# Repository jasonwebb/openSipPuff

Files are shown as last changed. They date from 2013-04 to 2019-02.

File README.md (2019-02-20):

# openSip+Puff

__openSip+Puff__ aims to provide a cheap, simple, open, and modern alternative input method based on the breath of a user that can be easily mapped to a variety of common actions like mouse clicks and keypresses.

The ultimate goal of this project is to go beyond simple utilitarian functionality and provide a new modality for creative expression that is meaningful for people with or without limited mobility. For me this means musical expression and visual art applications, but you are welcome to take it in whatever direction you want!

In contrast to other DIY sip-and-puff solutions, this project aims to keep the number of parts and assembly steps to a minimum while keeping the focus entirely on the digitization of breath - nothing more, nothing less. The hope is that this device can be manufactured as a true "plug-and-play", standalone device such that the only remaining steps that users will need to complete on their own are to (1) pop the board into an enclosure, (2) attach a mouthpiece with tubing, and (3) plug in a USB cable. With the help of native USB HID functionality, this device should (theoretically) be as easy to set up as any keyboard or mouse - no special drivers needed!

In keeping the focus tight and the parts count low it is expected that this device will be possible to sell for under $100 (ideally around $60). Fewer external parts also means fewer points of failure, so the device should last a while with minimal need for maintenance.

## Features
### Hardware
* ATmega32u4 microcontroller running the [Arduino Leonardo bootloader](https://www.arduino.cc/en/Main/ArduinoBoardLeonardo), allowing for the device to work as a standard USB HID device (mouse, keyboard, MIDI, etc) without any special drivers.
* [MPXV7007GP](https://www.digikey.com/product-detail/en/nxp-usa-inc/MPXV7007GP/MPXV7007GP-ND/1168441) analog pressure sensor for detecting direction and strength of sips and puffs.
* USB mini-B port so it can be connected to any PC
* 4-pin I2C interface for future expansion (may be removed if a good use case isn't identified)

### Firmware
```
TODO:
=====
  1. Sips and puffs need to be associated with actions (keypresses, mouse clicks, MIDI notes, etc) using some 
     sort of persistent data structure that can be loaded from EEPROM when the device is powered on.
  2. Patterns of sips and puffs should also be supported at some point. For example, one puff for left mouse 
     click, two puffs for right mouse click.
  3. Output raw analog values as serial data over USB to be transformed into other interesting actions by custom 
     applications or something like Wekinator.
  4. Output analog data as MIDI CC changes so the device can be used for expressive musical applications.
```

### Software
```
TODO:
=====
To make it easy for non-technical users to reconfigure the device, some sort of easy-to-use desktop application 
should be built. 

Once the firmware is worked out, I'd like to experiment with using Electron and modern web technologies to build 
this interface. 
```

### Mechanical
```
TODO:
=====
Connecting a plain plastic tube directly the sensor is fine for prototyping, but is not hygienic for real-world 
users. Some sort of easy-to-replace filter(s) should be added to capture saliva and particulates before they 
reach the sensor. 

I don't know much about these sorts of filters, so if you have some experience or ideas please send them to me!
```

## Similar projects
When I started building this project there weren't any other viable DIY sip-and-puff interfaces out there, but in the past year so a few great projects have sprung up that are worth looking at!

* [LipSync](https://github.com/makersmakingchange/LipSync) - uses an Arduino Pro Micro board and the [MPXV7002DPT1](https://www.digikey.com/product-detail/en/nxp-usa-inc/MPXV7002DPT1/MPXV7002DPT1CT-ND/3524215) sensor, as well as an optional Bluetooth breakout board. Includes a custom mouth-operated joystick built using 3D-printed parts and FSRs, all housed in a 3D-printed enclosure. _Incredible_ documentation, and available as a kit or fully assembled through [Makers Making Change](https://www.makersmakingchange.com/project/lipsync/).
* [FLipMouse](https://github.com/asterics/FLipMouse) - uses a Teensy LC and the [MPXV7007GP](https://www.digikey.com/product-detail/en/nxp-usa-inc/MPXV7007GP/MPXV7007GP-ND/1168441) sensor. Includes a custom mouth-operated joystick that is nearly identical to LipSync, all housed in a laser-cut acrylic enclosure. Available as a kit through [Hackerspace Shop](https://hackerspaceshop.com/products/flipmouse-diy-kit).
* [The 'Sup](https://www.instructables.com/id/The-Sup-a-Mouse-for-Quadriplegics-Low-Cost-and-Ope/) - uses an Arduino Pro Micro and a [MPXV7002DP](https://www.ebay.com/itm/MD-PS002-MPXV7002DP-Transducer-Pressure-Sensor-Differential-Breakout-Board-/401602810835?oid=202106155765) sensor on a breakout board, as well as an off-the-shelf [two-axis joystick module](https://www.ebay.com/itm/Module-PS2-Lever-Hots-Two-axis-Sensor-Joystick-Game-Controller/302615277464?hash=item467546af98:g:eGQAAOSwKXdaadFS). Features a unique 3D-printed mouthpiece that couples the joystick and tubing, though no filters are used.

## License
This work is licensed under a [Creative Commons Attribution-NonCommercial-ShareAlike 4.0 International License](http://creativecommons.org/licenses/by-nc-sa/4.0/).

Use this project to learn, tinker and share with friends. You are completely free to build this project for individuals  who need it. Small commercial runs for workshops or other educational uses are also completely cool.

The only reason that a fully-permissive open-source license is not used is to discourage, however naively, abuse through mass production and sale of this project by companies who are not as passionate about the quality and core mission of the project. If you're interested in producing and distributing this project to larger markets, please contact me and maybe we can collaborate!



## Media

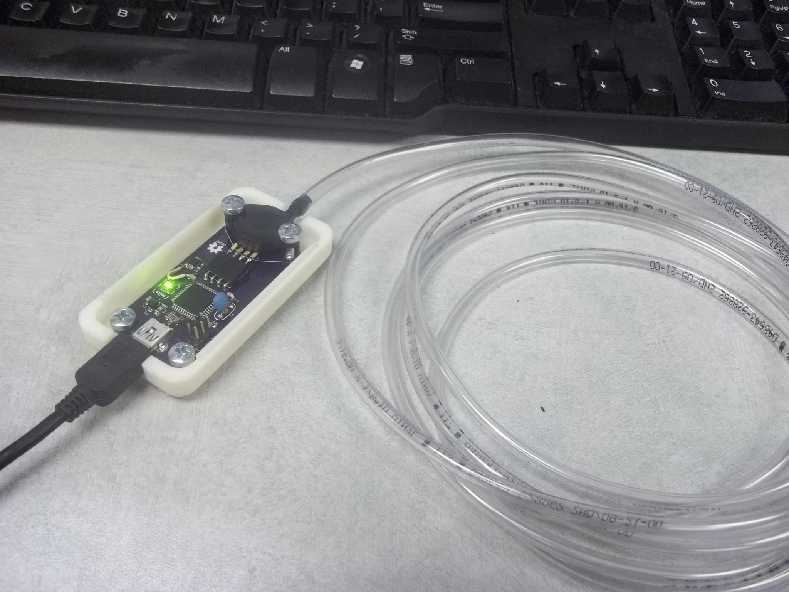
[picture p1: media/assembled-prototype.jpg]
Assembled prototype


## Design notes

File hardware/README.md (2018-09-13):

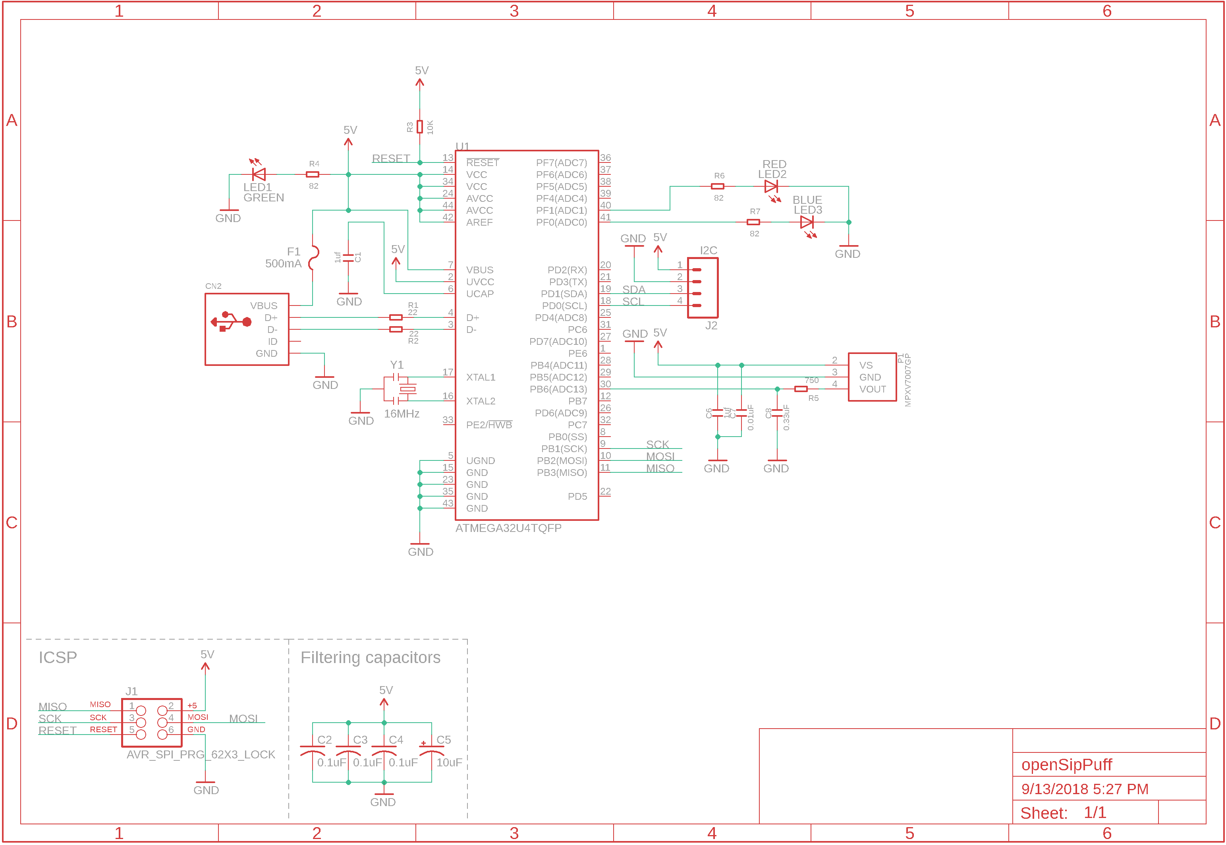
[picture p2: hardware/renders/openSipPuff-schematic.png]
Schematic


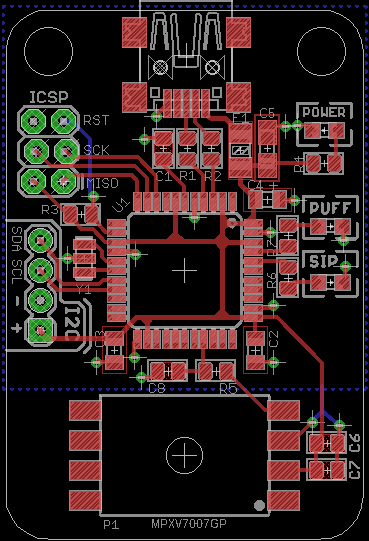
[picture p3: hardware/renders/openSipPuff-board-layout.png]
Board layout


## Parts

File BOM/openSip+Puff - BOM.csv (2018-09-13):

ID | Specifications | Purpose | Cost @ 1 | Cost @ 25 | Cost @ 50 | Cost @ 100 | Part number | URL
C1 | 1uF capacitor (0805) | USB smoothing cap for U1 | $0.28 | $0.19 | $0.19 | $0.11 | 399-8003-1-ND | https://www.digikey.com/product-detail/en/kemet/C0805C105K3PACTU/399-8003-1-ND/3471726
C2 | 0.1uF capacitor (0805) | Power smoothing for U1 | $0.30 | $0.21 | $0.21 | $0.10 | 709-1185-1-ND | https://www.digikey.com/product-detail/en/johanson-dielectrics-inc/250R15W104KV4T/709-1185-1-ND/1859517
C3 | 0.1uF capacitor (0805) | Power smoothing for U1 | $0.30 | $0.21 | $0.21 | $0.10 | 709-1185-1-ND | https://www.digikey.com/product-detail/en/johanson-dielectrics-inc/250R15W104KV4T/709-1185-1-ND/1859517
C4 | 0.1uF capacitor (0805) | Power smoothing for U1 | $0.30 | $0.21 | $0.21 | $0.10 | 709-1185-1-ND | https://www.digikey.com/product-detail/en/johanson-dielectrics-inc/250R15W104KV4T/709-1185-1-ND/1859517
C5 | 10uF polarized tantalum capacitor (1206) | Input power smoothing | $0.41 | $0.28 | $0.28 | $0.17 | 399-3683-1-ND | https://www.digikey.com/product-detail/en/kemet/T491A106K006AT/399-3683-1-ND/819008
C6 | 1uF capacitor (0805) | Power smoothing for P1 | $0.28 | $0.19 | $0.19 | $0.11 | 399-8003-1-ND | https://www.digikey.com/product-detail/en/kemet/C0805C105K3PACTU/399-8003-1-ND/3471726
C7 | 0.01uF capactor (0805) | Power smoothing for P1 | $0.48 | $0.33 | $0.33 | $0.20 | 399-7990-1-ND | https://www.digikey.com/product-detail/en/kemet/C0805C103J3GACTU/399-7990-1-ND/3471713
C8 | 0.33uF capacitor (0805) | Low-pass filter for P1 | $0.20 | $0.15 | $0.15 | $0.07 | 1276-1797-1-ND | https://www.digikey.com/product-detail/en/samsung-electro-mechanics/CL21B334KOCNNNC/1276-1797-1-ND/3889883
CN1 | USB mini-B | USB connector | $0.54 | $0.50 | $0.41 | $0.39 | 151-1206-1-ND | https://www.digikey.com/product-detail/en/edac-inc/690-005-299-043/151-1206-1-ND/4312192
F1 | 500mA PTC fuse | Protect board from spikes over USB, and USB from shorts | $0.13 | $0.13 | $0.11 | $0.10 | 507-1799-1-ND | https://www.digikey.com/product-detail/en/bel-fuse-inc/0ZCJ0025AF2E/507-1799-1-ND/4156322
J1 | 2x3 header (left blank) | ICSP interface
J2 | 1x4 header (left blank) | I2C breakout interface
LED1 | 20mA @ 2V green LED (0805) | Power indicator LED (green) | $0.31 | $0.17 | $0.17 | $0.12 | 160-1426-1-ND | https://www.digikey.com/product-detail/en/lite-on-inc/LTST-C171KGKT/160-1426-1-ND/386798
LED2 | 20mA @ 2V red LED (0805) | Sip indicator LED (red) | $0.35 | $0.19 | $0.19 | $0.13 | 160-1415-1-ND | https://www.digikey.com/product-detail/en/lite-on-inc/LTST-C170KRKT/160-1415-1-ND/386778
LED3 | 20mA @ 3.3V blue LED (0805) | Puff indicator LED (blue) | $0.50 | $0.28 | $0.28 | $0.18 | 160-1645-1-ND | https://www.digikey.com/product-detail/en/lite-on-inc/LTST-C171TBKT/160-1645-1-ND/573585
P1 | MPXV7007GP | Pressure sensor | $17.70 | $13.42 | $13.05 | $13.05 | MPXV7007GP-ND | https://www.digikey.com/products/en?keywords=mpxv7007gp
R1 | 22ohm resistor (0805) | USB termination resistors | $0.10 | $0.05 | $0.05 | $0.02 | 311-22.0CRCT-ND | https://www.digikey.com/product-detail/en/yageo/RC0805FR-0722RL/311-22.0CRCT-ND/730682
R2 | 22ohm resistor (0805) | USB termination resistors | $0.10 | $0.05 | $0.05 | $0.02 | 311-22.0CRCT-ND | https://www.digikey.com/product-detail/en/yageo/RC0805FR-0722RL/311-22.0CRCT-ND/730682
R3 | 10k resistor (0805) | RESET line pullup | $0.17 | $0.14 | $0.14 | $0.05 | RNCF0805DTE10K0CT-ND | https://www.digikey.com/product-detail/en/stackpole-electronics-inc/RNCF0805DTE10K0/RNCF0805DTE10K0CT-ND/2687083
R4 | 150ohm resistor (0805) | Current limit for LED1 | $0.10 | $0.09 | $0.09 | $0.03 | RHM150KCT-ND | https://www.digikey.com/product-detail/en/rohm-semiconductor/ESR10EZPJ151/RHM150KCT-ND/1762967
R5 | 750ohm resistor (0805) |  | $0.36 | $0.30 | $0.30 | $0.12 | P750DACT-ND | https://www.digikey.com/product-detail/en/panasonic-electronic-components/ERA-6AEB751V/P750DACT-ND/1465944
R6 | 150ohm resistor (0805) | Current limit for LED2 | $0.10 | $0.09 | $0.09 | $0.03 | RHM150KCT-ND | https://www.digikey.com/product-detail/en/rohm-semiconductor/ESR10EZPJ151/RHM150KCT-ND/1762967
R7 | 84.5ohm resistor (0805) | Current limit for LED3 | $0.10 | $0.06 | $0.06 | $0.02 | 311-84.5CRCT-ND | https://www.digikey.com/product-detail/en/yageo/RC0805FR-0784R5L/311-84.5CRCT-ND/731119
U1 | ATMega32u4 | Microcontroller | $4.20 | $3.85 | $3.85 | $3.49 | ATMEGA32U4-AURCT-ND | https://www.digikey.com/product-detail/en/microchip-technology/ATMEGA32U4-AUR/ATMEGA32U4-AURCT-ND/3440960
Y1 | 16MHz resonator | Resonator for microcontoller | $0.30 | $0.25 | $0.22 | $0.20 | 490-17948-1-ND | https://www.digikey.com/product-detail/en/murata-electronics-north-america/CSTNE16M0V530000R0/490-17948-1-ND/8747756
 |  | Total | $27.61 | $21.28 | $20.79

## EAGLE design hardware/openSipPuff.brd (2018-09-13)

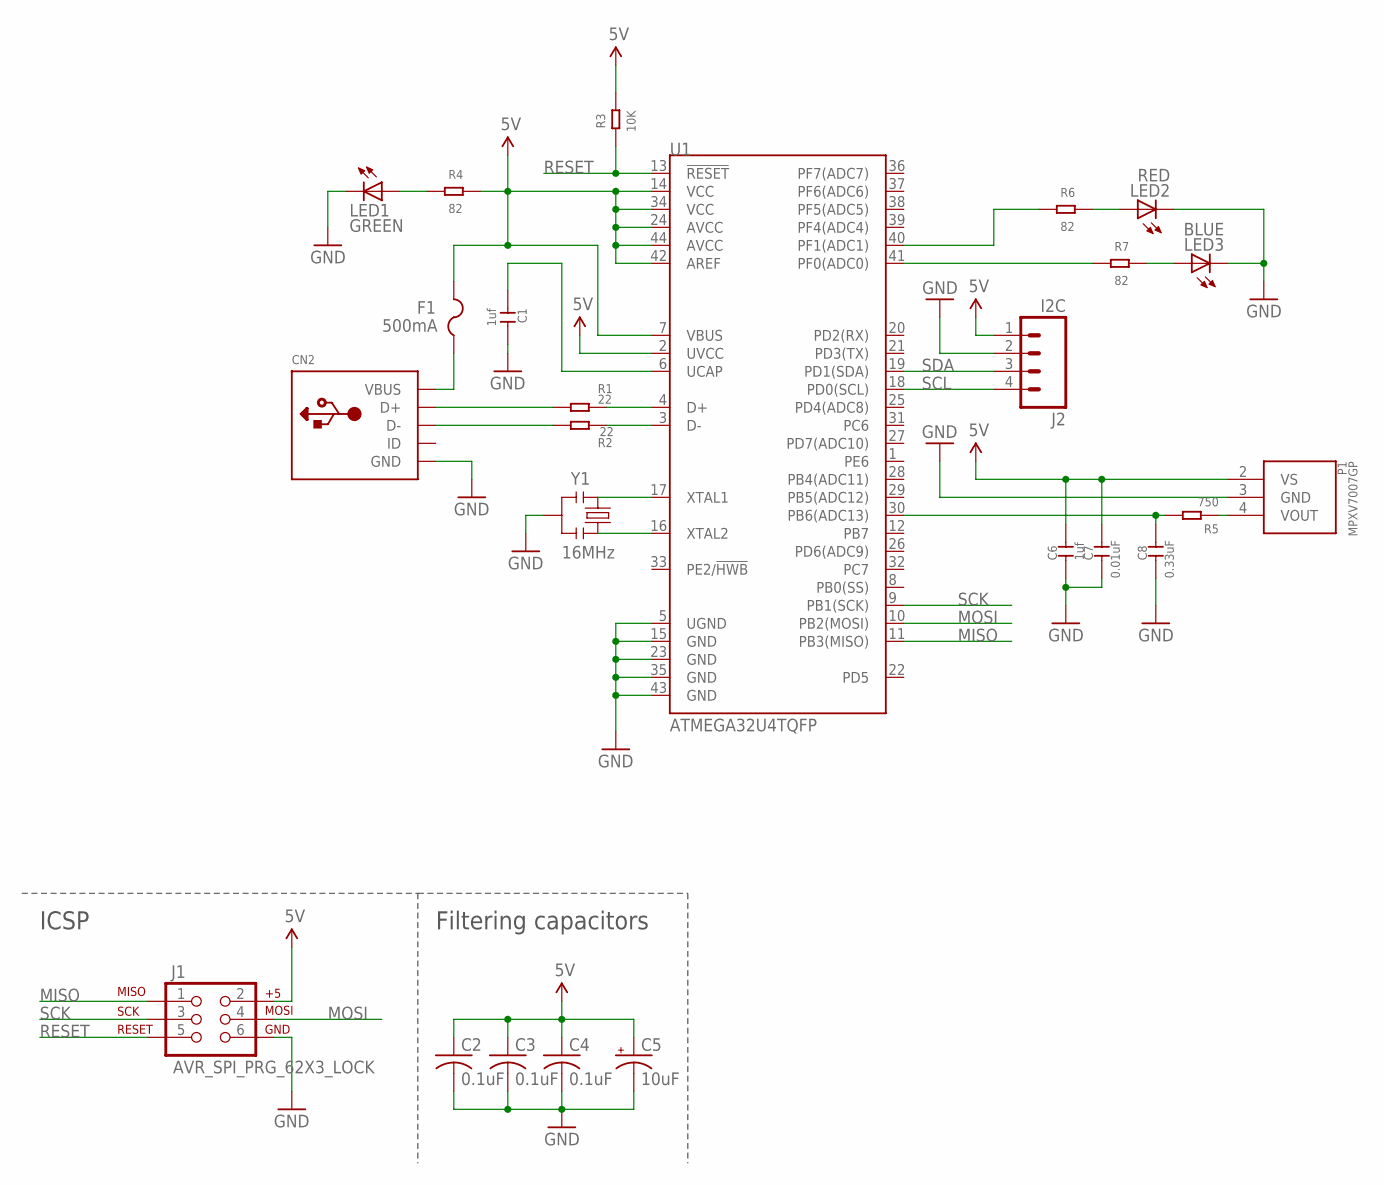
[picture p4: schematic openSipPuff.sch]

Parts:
C1, C6: 1uf; C0805
C2, C3, C4: 0.1uF; C0805K
C5: 10uF; A/3216-18R
C7: 0.01uF; C0805
C8: 0.33uF; C0805
CN2: USBMINIB; USB-MINIB
F1: 500mA; R1206
J1: AVR_SPI_PRG_62X3_LOCK; 2X3_LOCK
J2: I2C; 1X04
LED1: GREEN; CHIPLED_0805
LED2: RED; CHIPLED_0805
LED3: BLUE; CHIPLED_0805
P1: MPXV7007GP; SOP8
R1, R2: 22; R0805
R3: 10K; R0805
R4, R6, R7: 82; R0805
R5: 750; R0805
U1: ATMEGA32U4TQFP; SPARKFUN-DIGITALIC_TQFP44
Y1: 16MHz; RESONATOR-SMD

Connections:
5V: C2.1, C3.1, C4.1, C5.+, C6.2, C7.2, F1.2, J1.2, J2.1, P1.2 (VS), R3.2, R4.2, U1.2 (UVCC), U1.7 (VBUS), U1.14 (VCC), U1.24 (AVCC), U1.34 (VCC), U1.42 (AREF), U1.44 (AVCC)
D+: CN2.D+, R1.1
D-: CN2.D-, R2.1
GND: C1.2, C2.2, C3.2, C4.2, C5.-, C6.1, C7.1, C8.1, CN2.GND, J1.6, J2.2, LED1.C, LED2.C, LED3.C, P1.3 (GND), U1.5 (UGND), U1.15 (GND), U1.23 (GND), U1.35 (GND), U1.43 (GND), Y1.2
MISO: J1.1, U1.11 (PB3(MISO))
MOSI: J1.4, U1.10 (PB2(MOSI))
unnamed: R1.2, U1.4 (D+)
unnamed: R2.2, U1.3 (D-)
unnamed: C1.1, U1.6 (UCAP)
unnamed: CN2.VBUS, F1.1
unnamed: U1.17 (XTAL1), Y1.1
unnamed: U1.16 (XTAL2), Y1.3
unnamed: C8.2, R5.2, U1.30 (PB6(ADC13))
unnamed: R6.1, U1.40 (PF1(ADC1))
unnamed: R7.1, U1.41 (PF0(ADC0))
unnamed: P1.4 (VOUT), R5.1
unnamed: LED1.A, R4.1
unnamed: LED3.A, R7.2
unnamed: LED2.A, R6.2
RESET: J1.5, R3.1, U1.13 (!RESET)
SCK: J1.3, U1.9 (PB1(SCK))
SCL: J2.4, U1.18 (PD0(SCL))
SDA: J2.3, U1.19 (PD1(SDA))

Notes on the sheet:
ICSP
Filtering capacitors

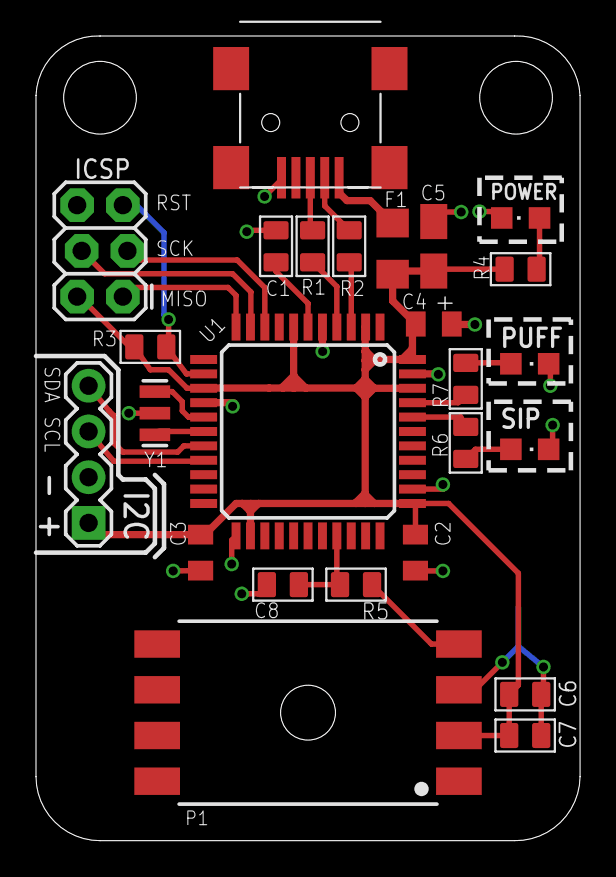
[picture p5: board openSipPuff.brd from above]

Board: 2 copper layers, 30.2 x 44.7 mm, 25 parts (0 on the bottom side), 23 nets.

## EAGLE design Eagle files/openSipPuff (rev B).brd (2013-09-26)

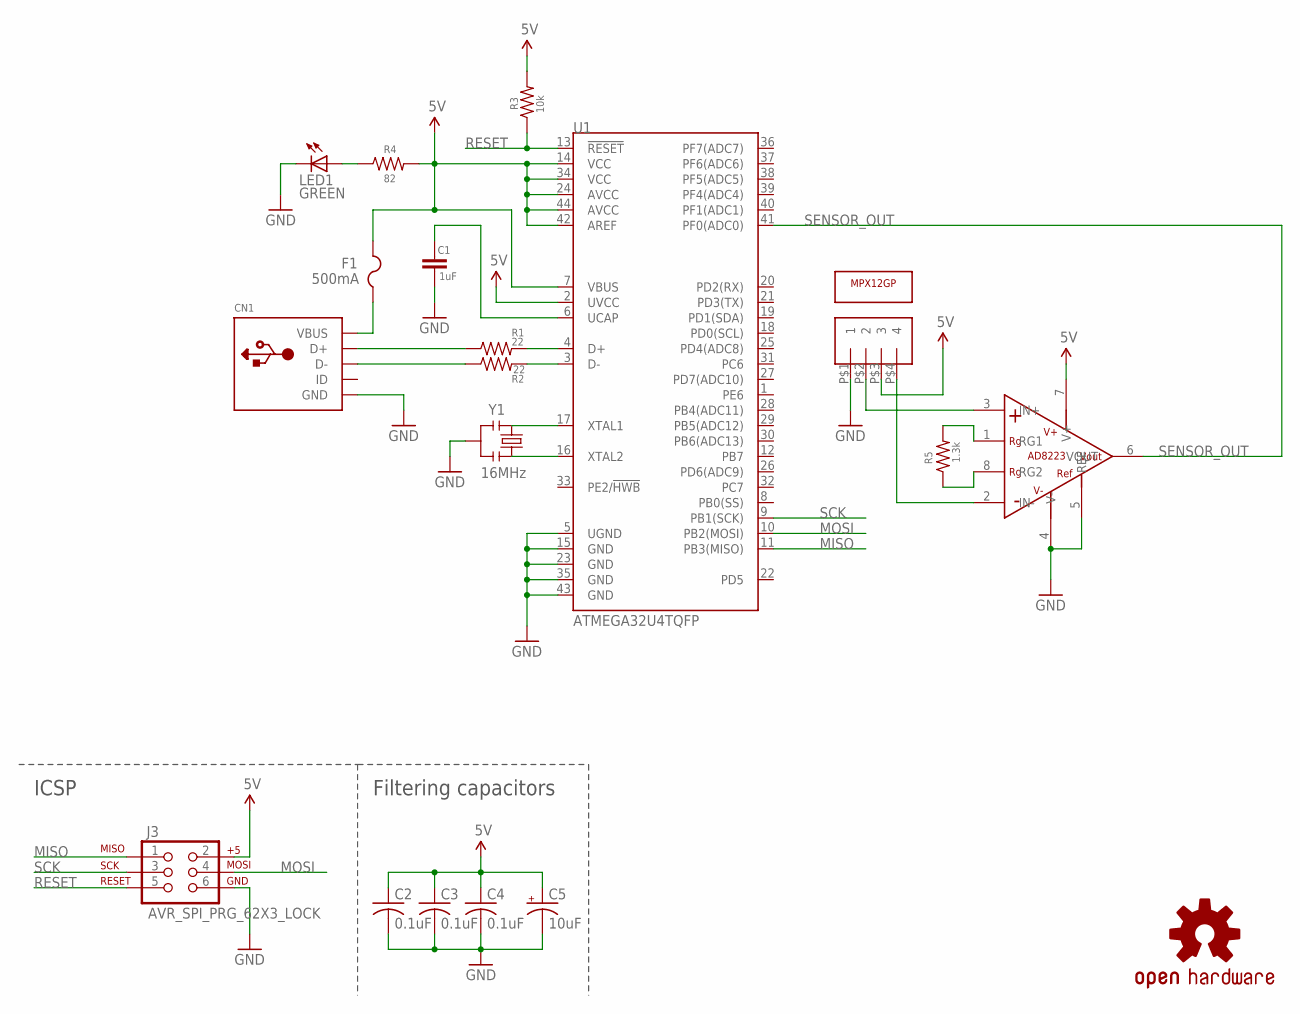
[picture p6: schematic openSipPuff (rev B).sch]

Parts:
C1: 1uF; 0805
C2, C3, C4: 0.1uF; C0805K
C5: 10uF; A/3216-18R
CN1: USBMOLEX; USB-MINIB-THM-MOLEX
F1: 500mA; R1206
J2: 1X04-RA
J3: AVR_SPI_PRG_62X3_LOCK; 2X3_LOCK
LED1: GREEN; CHIPLED_0805
LOGO1: OSHW-LOGOM; OSHW-LOGO-M
R1, R2: 22; 0805
R3: 10k; 0805
R4: 82; 0805
R5: 1.3k; 0805
U1: ATMEGA32U4TQFP; SPARKFUN-DIGITALIC_TQFP44
U2: AD8223; MSOP-8
U3: MPX12GP
Y1: 16MHz; RESONATOR-PTH

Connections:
5V: C2.1, C3.1, C4.1, C5.+, F1.2, J2.P$3 (3), J3.2, R3.2, R4.2, U1.2 (UVCC), U1.7 (VBUS), U1.14 (VCC), U1.24 (AVCC), U1.34 (VCC), U1.42 (AREF), U1.44 (AVCC), U2.7 (V+)
D+: CN1.D+, R1.1
D-: CN1.D-, R2.1
GND: C1.2, C2.2, C3.2, C4.2, C5.-, CN1.GND, J2.P$1 (1), J3.6, LED1.C, U1.5 (UGND), U1.15 (GND), U1.23 (GND), U1.35 (GND), U1.43 (GND), U2.4 (V-), U2.5 (REF), Y1.2
MISO: J3.1, U1.11 (PB3(MISO))
MOSI: J3.4, U1.10 (PB2(MOSI))
unnamed: R1.2, U1.4 (D+)
unnamed: R2.2, U1.3 (D-)
unnamed: C1.1, U1.6 (UCAP)
unnamed: CN1.VBUS, F1.1
unnamed: U1.17 (XTAL1), Y1.1
unnamed: U1.16 (XTAL2), Y1.3
unnamed: R5.2, U2.1 (RG1)
unnamed: J2.P$2 (2), U2.3 (IN+)
unnamed: R5.1, U2.8 (RG2)
unnamed: LED1.A, R4.1
unnamed: J2.P$4 (4), U2.2 (IN-)
RESET: J3.5, R3.1, U1.13 (!RESET)
SCK: J3.3, U1.9 (PB1(SCK))
SENSOR_OUT: U1.41 (PF0(ADC0)), U2.6 (VOUT)

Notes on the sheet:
ICSP
Filtering capacitors

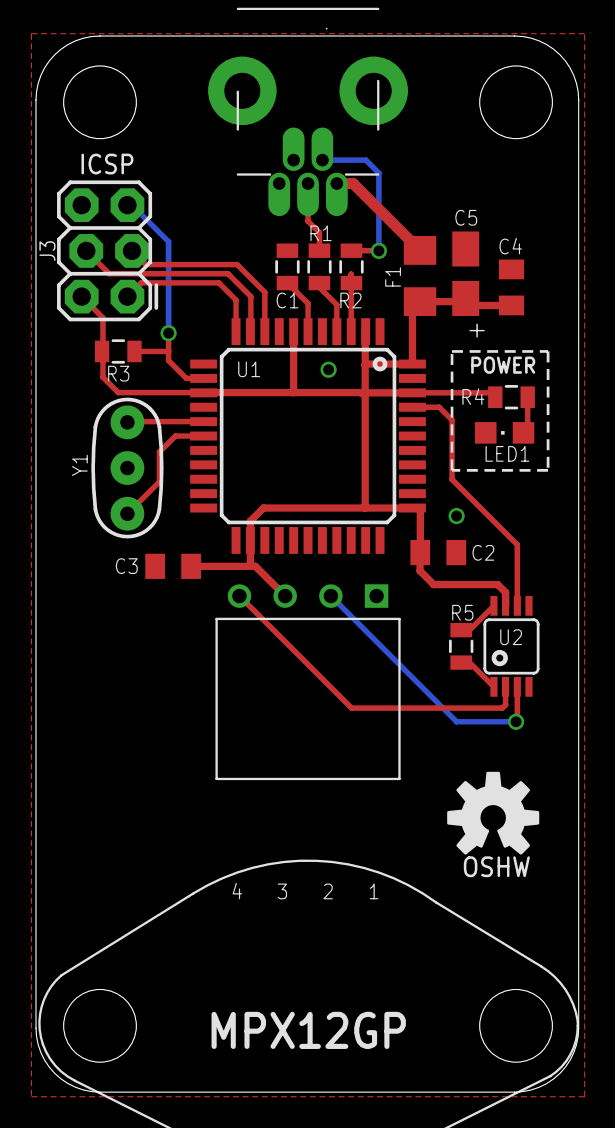
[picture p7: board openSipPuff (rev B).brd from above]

Board: 2 copper layers, 30.1 x 58.7 mm, 20 parts (0 on the bottom side), 20 nets.

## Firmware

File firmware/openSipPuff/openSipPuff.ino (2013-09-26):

/*******************************************************************************************
 openSip+Puff main sketch
 
 Last revision: 9/16/2013
 Author: Jason Webb
 Author's website: http://jason-webb.info
 Project wiki: http://jason-webb.info/wiki/index.php?title=OpenSip%2BPuff
 
 Description:
 ============
 Highly expressive, reconfigurable breath interface that performs native USB keyboard
 and mouse actions based on user-defined associations with "sipping" and "puffing"
 detected with a pressure transducer.
 
 Mode flag byte:
 ===============
 The very first byte stored in EEPROM (address 0) sets the mode of the device, and can 
 be any of the following:
 
 [B] = basic mode - sip and puff
 [F] = fine mode - soft and hard sips and puffs
 [P] = pattern mode - pattern of sips and puffs
 
 Command packet structure:
 =========================
 Keyboard command: [P|S],[S|H],K,[number of keys],[key #1],...,[key n],255
 Mouse command: [P|S],[S|H],M,[C|M|D],[parameter #1],...,[parameter n],255
 
 Parameter legend:
 =================
 [P|S] = puff or sip
 [S|H] = soft or hard
 [K] = keyboard action
 [M] = mouse action
 [C|M|D] = click, move, drag
 [key] = ASCII value of key to press (keyboard modifiers are also valid: http://arduino.cc/en/Reference/KeyboardModifiers)
 [parameter] = interpretation depends on selected action type
 255 = indicates end of command

 Examples:
 =========
 1) Press "return" key on soft sip = S,S,K,1,KEY_RETURN,255
 2) Press "Win + R" on hard puff = P,H,K,2,KEY_GUI_LEFT,r,255
 3) Click left mouse button on soft puff = P,S,M,C,1,255
 4) Move mouse position up 5 units on hard sip = S,H,M,M,0,5,0,255
 5) Click left mouse button and drag left 5 units on soft sip = S,S,M,D,1,-5,0,0,255
 
 Uses
 =====
 1) FPS controls = crouch (CTRL), jump (space), reload (r), fire (left mouse)
 2) Rotate 3D model = click mouse button and drag along one or more axes
 3) Launch programs = install AutoHotKey, assign programs to special keyboard combinations
 4) Turn volume up/down = install AutoHotKey, assign OS volume to special keyboard combinations
 
*******************************************************************************************/

#include <EEPROM.h>    // EEPROM library used for storing configuration between uses

// Sensor pin and readings
int sensorPin = 5;              // Analog pin 5 (PF0/ADC0)
const int numReadings = 10;     // Number of readings to buffer
int sensorValues[numReadings];  // Buffer of readings
int sensorAverage;              // Average of all readings in buffer
int sensorBaseValue = 457;      // Value of sensor with no input

// Sip and puff detection variables
int basicThreshold = 150;              // Threshold used for binary sip and puff
int softThreshold = 150;               // Threshold used for "soft" sips and puffs
int hardThreshold = 250;               // Threshold used for "hard" sips and puffs
boolean sipThresholdCrossed = false;   // Data crossed lower basic threshold
boolean puffThresholdCrossed = false;  // Data crossed upper basic threshold
int currentPeak = 0;                   // Records peaks

// Action detection flags
boolean sipDetected = false;    // Goes "true" when sip is detected
boolean puffDetected = false;   // Goes "false" when puff is detected

// General program behavior
boolean debug = false;

// EEPROM command variables
const int maxCommandLength = 10;
byte incomingCommand[maxCommandLength];  // Command buffer from EEPROM
byte commandDelimiter = 255;             // End of command delimiter
byte commandIndex = 0;                   // Current index within command being read
byte value = -1;                         // Most recent byte read from EEPROM
byte nextValue = -1;                     // Next byte found in EEPROM after value
byte currentAddress = 1;                 // Always start at 1, mode flag is at 0

// Commands (basic mode)
byte commandSip[maxCommandLength];    // Command to execute on sip
byte commandPuff[maxCommandLength];   // Command to execute on puff

// Commands (fine mode)
byte commandSipSoft[maxCommandLength];   // Command to execute on sip (soft)
byte commandSipHard[maxCommandLength];   // Command to execute on sip (hard)
byte commandPuffSoft[maxCommandLength];  // Command to execute on puff (soft)
byte commandPuffHard[maxCommandLength];  // Command to execute on puff (hard)

// Input mode
const byte MODE_BASIC = 0;  // Basic mode = only sip and puff
const byte MODE_FINE = 1;   // Fine mode = hard and soft sips/puffs
byte mode;                  // Current mode;

// Serial communication variables
byte etIn[3];               // Incoming handshake buffer
byte et[] = {'E','T','?'};  // Key to check handshake against

void setup() {
  // Set up the sensor
  pinMode(sensorPin, INPUT);
  
  // Initialize the various serial streams
  Serial.begin(9600);
  Keyboard.begin();
  Mouse.begin();
  
  // Write some fake commands to EEPROM
  // Address 0 = mode flag
  EEPROM.write(0,'F');  // Basic mode
  
  // Sip (hard) = press return key
  // S,H,K,1,32,255
  EEPROM.write(1,'S');  // Sip
  EEPROM.write(2,'H');  // Hard
  EEPROM.write(3,'K');  // Keyboard
  EEPROM.write(4,1);    // 1 parameter
  EEPROM.write(5,KEY_RETURN);  // h
  EEPROM.write(6,255);  // End
  
  // Sip (soft) = Alt + Tab
  // S,S,K,1,50,255
  EEPROM.write(7,'S');           // Sip
  EEPROM.write(8,'S');           // Soft
  EEPROM.write(9,'K');           // Keyboard
  EEPROM.write(10,2);             // 1 parameter
  EEPROM.write(11,KEY_LEFT_ALT); // Left alt
  EEPROM.write(12,KEY_TAB);      // Tab
  EEPROM.write(13,255);          // End

  // Puff (hard) = click and drag
  // P,H,M,D,10,0,0,255
  EEPROM.write(14,'P');  // Puff
  EEPROM.write(15,'H');  // Hard
  EEPROM.write(16,'M');  // Mouse
  EEPROM.write(17,'D');  // Click
  EEPROM.write(18,1);    // Left click
  EEPROM.write(19,10);   // x = 40
  EEPROM.write(20,0);    // y = 0
  EEPROM.write(21,0);    // scroll = 0
  EEPROM.write(22,255);  // End
  
  // Puff (soft) = Alt + F4
  // P,S,K,2,KEY_LEFT_ALT,KEY_F4
  EEPROM.write(23,'P');
  EEPROM.write(24,'S');
  EEPROM.write(25,'K');
  EEPROM.write(26,1);
//  EEPROM.write(27,KEY_LEFT_ALT);
//  EEPROM.write(28,KEY_F4);
  EEPROM.write(27,'a');
  EEPROM.write(28,255);
  
  delay(4000); 
  loadCommands();
}

void loop() {
  processSerial();   // Process incoming serial communication
  readSensor();      // Take readings from the sensor
  processSensor();   // Look for "sips" and "puffs" in the sensor readings
  
  // Sip has been detected
  if(sipDetected) {
    // Hard sip detected
    if(currentPeak <= sensorBaseValue - hardThreshold) {
      Serial.print("# Sip (hard) detected - ");
      
      switch(mode) {
        case MODE_BASIC:
          executeCommand(commandSip);
          break;
        case MODE_FINE:
          executeCommand(commandSipHard);
          break;
      }
      
    // Soft sip detected
    } else if(currentPeak <= sensorBaseValue - softThreshold) {
      Serial.print("# Sip (soft) detected - ");
      
      switch(mode) {
        case MODE_BASIC:
          executeCommand(commandSip);
          break;
        case MODE_FINE:
          executeCommand(commandSipSoft);
          break;
      }
    }
      
    Serial.println(currentPeak);
    currentPeak = sensorBaseValue;
    sipDetected = false;
  }
  
  // Puff has been detected
  if(puffDetected) {
    // Hard puff detected
    if(currentPeak >= sensorBaseValue + hardThreshold) {
      Serial.print("# Puff (hard) detected - ");
      
      switch(mode) {
        case MODE_BASIC:
          executeCommand(commandPuff);
          break;
        case MODE_FINE:
          executeCommand(commandPuffHard);
          break;
      }
      
    // Soft puff detected
    } else if(currentPeak >= sensorBaseValue + softThreshold) {
      Serial.print("# Puff (soft) detected - ");
      
      switch(mode) {
        case MODE_BASIC:
          executeCommand(commandPuff);
          break;
        case MODE_FINE:
          executeCommand(commandPuffSoft);
          break;
      }
    }
    
    Serial.println(currentPeak);
    currentPeak = sensorBaseValue;
    puffDetected = false;
  }
  
  // Output the raw sensor readings
  if(debug)
    Serial.println(sensorAverage);
}

/* ========================================================================================
   SENSOR FUNCTIONS
============================================================================================ */

/*************************************************
 readSensor()
 
 Read sensor value several times, store average 
 in globally-accessible variable.
**************************************************/
void readSensor() {
  // Take a few readings
  for(int i=0; i<numReadings; i++) {
    int v = analogRead(sensorPin);
    sensorValues[i] = v;
  }
  
  // Find average of all readings
  int total = 0;
  for(int i=0; i<numReadings; i++)
    total += sensorValues[i];
    
  sensorAverage = total/numReadings;
}

/*****************************************************
 processSensor()
 
 Derive sip and puff activity from sensor data
******************************************************/
void processSensor() {
  // While data is hovering in safe zone ...
  if(sipThresholdCrossed == false && puffThresholdCrossed == false) {
    
    // Wait for the data to cross the basic threshold
    if(sensorAverage <= sensorBaseValue - basicThreshold) {
      sipThresholdCrossed = true;
      currentPeak = sensorAverage;
    } else if(sensorAverage >= sensorBaseValue + basicThreshold) {
      puffThresholdCrossed = true;
      currentPeak = sensorAverage;
    }
    
  // If data has drifted above or below safe zone
  } else {
    
    // Record peaks
    if(sipThresholdCrossed)
      if(sensorAverage < currentPeak)
        currentPeak = sensorAverage;
        
    if(puffThresholdCrossed)
      if(sensorAverage > currentPeak)
        currentPeak = sensorAverage;
    
    // Check if the data has returned to safe zone, then trigger a sip or puff
    if(sensorAverage <= sensorBaseValue + basicThreshold && sensorAverage >= sensorBaseValue - basicThreshold) {
      // Sip detected
      if(sipThresholdCrossed) {
        sipDetected = true;
        sipThresholdCrossed = false;
      }
      
      // Puff detected
      if(puffThresholdCrossed) {
        puffDetected = true;
        puffThresholdCrossed = false;
      }
    }
  }
}

/* ========================================================================================
   COMMAND FUNCTIONS
============================================================================================ */
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

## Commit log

2013-04-15 Eagle files for Rev A and updated README
    [openSipPuff (rev A).brd, openSipPuff (rev A).sch]
2013-09-26 Firmware update and rev B Eagle files
    [openSipPuff (rev B).brd, openSipPuff (rev B).sch]
2013-09-27 Updated BOM for rev B iteration
    [Board BOM.xlsx, openSip+Puff (rev B) - BOM.xlsx]
2013-09-27 Updated 3D files with new SCAD file and STLs
    [Clamshell case.scad, Full housing with mouse ears.stl, Full housing without mouse ears.stl, Lower half with mouse ears.stl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]
2014-08-28 Rev C updates
    New Eagle files and BOM.
    [openSip+Puff (rev B) - BOM.xlsx, openSipPuff (rev C) - BOM.xlsx, openSipPuff (rev C).brd, openSipPuff (rev C).sch]
2017-01-14 Renaming folders to be more semantic
    [Full housing with mouse ears.stl, Full housing without mouse ears.stl, Lower half with mouse ears.stl, Lower housing without mouse ears.stl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]
2017-01-14 Fixing folder name case (1/2)
    [Full housing with mouse ears.stl, Full housing without mouse ears.stl, Lower half with mouse ears.stl, Lower housing without mouse ears.stl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]
2017-01-14 Added latest BOM
    [openSip+Puff (rev B) BOM.csv]
2017-01-14 Updated BOM with CSV for web viewing
    [openSip+Puff (rev B) BOM.csv, openSipPuff (rev C) - BOM.csv]
2017-01-15 Updated BOM and removed references to ambiguous rev designation.
    [openSipPuff (rev C) - BOM.csv, openSipPuff (rev C) - BOM.xlsx, openSipPuff - bill of materials.csv, openSipPuff - bill of materials.xlsx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]
2018-09-13 Removing outdated enclosure files
    [Full housing with mouse ears.stl, Full housing without mouse ears.stl, Lower half with mouse ears.stl, Lower housing without mouse ears.stl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]
2018-09-13 Major board updates with new sensor, I2C interface, and more
    [openSipPuff.brd, openSipPuff.sch]
2018-09-13 Updating BOM to match latest design
    [openSip+Puff - BOM.csv, openSipPuff - bill of materials.csv]
2018-09-13 Removing outdated BOM
    [openSipPuff - bill of materials.xlsx]
2018-09-13 Fixing file names of board renders
2018-09-13 Adding custom library for MPXV7007GP pressure sensor
2018-09-13 Updating MPXV7007GP footprint to include hole for underside port
    [openSipPuff.brd, openSipPuff.sch]

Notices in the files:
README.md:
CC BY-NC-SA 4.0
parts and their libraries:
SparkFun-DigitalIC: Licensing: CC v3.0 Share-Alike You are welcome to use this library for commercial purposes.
